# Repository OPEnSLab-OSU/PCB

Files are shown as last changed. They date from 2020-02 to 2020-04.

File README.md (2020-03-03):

# Project List
Opens Staff - Clone this repo and make a folder for your PCB. Once your PCB is added, place project links and update board file links here 

## [EAGLE Library Files](https://github.com/OPEnSLab-OSU/PCB/tree/master/OPEnS_Library)
Managed Libraries Folder *Coming Soon*

<!-- Copy an existing entry and add your project links directly below this comment -->
## [Sapflow](https://github.com/OPEnSLab-OSU/OPEnS-Lab-Home/wiki/Sap-Flow-Meter)

**New* V3 Board [Sapflow](https://github.com/OPEnSLab-OSU/PCB/tree/master/Sapflow)

## [Evaporometer](https://github.com/OPEnSLab-OSU/OPEnS-Lab-Home/wiki/Evaporometer)

INA125P Load Cell Amp [DevBoard](https://github.com/OPEnSLab-OSU/PCB/tree/master/Evaporometer_Lite/INA125P)

**New* Evaporometer V2 [V2.2 Board](https://github.com/OPEnSLab-OSU/PCB/tree/master/Evaporometer_Lite)

## [Hypnos](https://github.com/OPEnSLab-OSU/OPEnS-Hypnos)

**New* V3 Board [Hypnos 12V](https://github.com/OPEnSLab-OSU/PCB/tree/master/Hypnos)

## [PNNL Flux Tool](https://github.com/OPEnSLab-OSU/PNNLFluxV1)

Head [board](https://github.com/OPEnSLab-OSU/PCB/blob/master/PNNLFlux/Head-Board/head-board.brd),
[schematic](https://github.com/OPEnSLab-OSU/PCB/blob/master/PNNLFlux/Head-Board/head-board.sch)

Rod [board](https://github.com/OPEnSLab-OSU/PCB/blob/master/PNNLFlux/Rod-Board/rod-board.brd),
[schematic](https://github.com/OPEnSLab-OSU/PCB/blob/master/PNNLFlux/Rod-Board/rod-board.sch)

MS580302 [Pressure/EC sensor](https://github.com/OPEnSLab-OSU/PCB/tree/master/PNNLFlux/MS5803-02BA)

## [SmartRock](https://github.com/OPEnSLab-OSU/SmartRock)

MS580302 Pressure [MS5803](https://github.com/OPEnSLab-OSU/PCB/tree/master/SmartRock/MS5803), 
HydroPCB [HydroPCB](https://github.com/OPEnSLab-OSU/PCB/tree/master/SmartRock/HydroPCB)

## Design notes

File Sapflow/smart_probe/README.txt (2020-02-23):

This PCB attatches to the Sapflow project probe and makes it "smart".
It has a 3-channel ADC with analog lowpass filters in front of the inputs. 
It also has a differential I2C driver chip which can send I2C data from
the ADC over CAT V cables a couple meters long.

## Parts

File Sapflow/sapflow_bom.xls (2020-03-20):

PCB | Qty | Value | Device | Package | Parts | Description | Price | PN | Link
Smart Probe | 40 |  | Red LED | CHIP-LED0805 | LED1 | Red LED | 0.145 | 1080-EAST2012RA1CT-ND | https://www.digikey.com/product-detail/en/everlight-electronics-co-ltd/EAST2012RA1/1080-EAST2012RA1CT-ND/11201058
Smart Probe | 15 |  | Green LED | CHIP-LED0805 | LED2 | Green LED | 0.18 | 732-4983-1-ND | https://www.digikey.com/product-detail/en/w%C3%BCrth-elektronik/150080GS75000/732-4983-1-ND/4489913
Smart Probe | 100 | 0.1u | C-USC0805 | C0805 | C4, C6, C7, C8 | CAPACITOR, American symbol | 0.0286 | 1276-6476-1-ND | https://www.digikey.com/product-detail/en/samsung-electro-mechanics/CL21B154KBFNNNG/1276-6476-1-ND/5958104
Smart Probe | 100 | 1.5k | R-US_R0805 | R0805 | R17 | RESISTOR, American symbol | 0.0091 | RMCF0805FT1R62CT-ND | https://www.digikey.com/product-detail/en/stackpole-electronics-inc/RMCF0805FT1R62/RMCF0805FT1R62CT-ND/2418313
Smart Probe | 100 | 100 | R-US_R0805 | R0805 | R7 | RESISTOR, American symbol | 0.0104 | RMCF0805FT100RCT-ND | https://www.digikey.com/product-detail/en/stackpole-electronics-inc/RMCF0805FT100R/RMCF0805FT100RCT-ND/1942332
Smart Probe | 100 | 1u | C-USC0805 | C0805 | C1, C2, C3 | CAPACITOR, American symbol | 0.0281 | 1276-6471-1-ND | https://www.digikey.com/product-detail/en/samsung-electro-mechanics/CL21B105KOFNNNG/1276-6471-1-ND/5958099
Smart Probe | 100 | 40k | R-US_R0805 | R0805 | R1, R2, R3, R4, R14, R15 | RESISTOR, American symbol | 0.0104 | RMCF0805FT39K0CT-ND | https://www.digikey.com/product-detail/en/stackpole-electronics-inc/RMCF0805FT39K0/RMCF0805FT39K0CT-ND/2418387
Smart Probe | 100 | 47uF | C-USC0805 | C0805 | C5 | CAPACITOR, American symbol | 0.067 | 1276-1100-1-ND | https://www.digikey.com/product-detail/en/samsung-electro-mechanics/CL21A226MQQNNNE/1276-1100-1-ND/3889186
Smart Probe | 100 | 5k | R-US_R0805 | R0805 | R10, R11, R16 | RESISTOR, American symbol | 0.0104 | RMCF0805FT5K10CT-ND | https://www.digikey.com/product-detail/en/stackpole-electronics-inc/RMCF0805FT5K10/RMCF0805FT5K10CT-ND/1942416
Smart Probe | 100 | 910 | R-US_R0805 | R0805 | R5, R6, R8, R9 | RESISTOR, American symbol | 0.0104 | RMCF0805FT909RCT-ND | https://www.digikey.com/product-detail/en/stackpole-electronics-inc/RMCF0805FT909R/RMCF0805FT909RCT-ND/1942369
Smart Probe | 12 | MCP3424-E_SL | MCP3424-E_SL | SOIC127P600X175-14N | IC1 | ADC 18-Bit 4-ch 2.048V I2C SOIC14 | 3.91 | MCP3424-E/SL-ND | https://www.digikey.com/product-detail/en/microchip-technology/MCP3424-E-SL/MCP3424-E-SL-ND/1680890
Flex Probe | 100 | 100 | R-US_R0603 | R0603 | Heater resistor | RESISTOR, American symbol | 0.0065 | RMCF0603FT100RCT-ND | https://www.digikey.com/product-detail/en/stackpole-electronics-inc/RMCF0603FT100R/RMCF0603FT100RCT-ND/1942965
Flex Probe | 75 | PT100 | R-US_R0603 | R0603 | RTD | 100-ohm RTD | 1.2188 | PTS0603100CT-ND | https://www.digikey.com/products/en?keywords=PTS0603100CT-ND
Main PCB | 12 |  | NMOSSOT223 | SOT223 | T2 | MOS FET | 0.613 | FDT439NCT-ND | https://www.digikey.com/products/en?keywords=FDT439NCT-ND
Main PCB | 12 | 33uF | CPOL-USD/7343-31R | D/7343-31R | C8 | POLARIZED CAPACITOR, American symbol | 0.72 | 478-3047-1-ND | https://www.digikey.com/products/en?keywords=478-3047-1-ND
Main PCB | 12 | 47uF | CPOL-USD/7343-31R | D/7343-31R | C7 | POLARIZED CAPACITOR, American symbol | 0.628 | 478-3936-1-ND | https://www.digikey.com/products/en?keywords=478-3936-1-ND
Main PCB | 100 | 100pF | C-USC0805 | C0805 | C2 | CAPACITOR, American symbol | 0.0087 | 399-15000-1-ND | https://www.digikey.com/product-detail/en/kemet/C0805C101JAGAC7800/399-15000-1-ND/7382549
Main PCB | 12 | CR1220 | BATTERYCR1220_SMT | CR1220 | B1 | CR1220 SMT - Digikey: 3001K-ND | 0.44 | 36-3001-ND | https://www.digikey.com/products/en?keywords=3001K-ND
Main PCB | 12 | DS3231ST&R | DS3231ST&R | 21-0042B_16 | RTC | DS3231 RTC IC only | 7.576 | DS3231SN#T&RCT-ND | https://www.digikey.com/products/en?keywords=DS3231SN%23T%26RCT-ND
Main PCB | 12 | MAXIM_MAX5033BASA+MAXIM_MAX5033BASA+_0_1 | MAXIM_MAX5033BASA+MAXIM_MAX5033BASA+_0_1 | MAXIM_MAX5033BASA+_1 | U1 | MAX-MAX5033-IL8 | 2.71 | MAX5033BASA+-ND | https://www.digikey.com/products/en?keywords=MAX5033BASA%2B-ND
Main PCB | 12 | MICROSD | MICROSD | MICROSD | MICROSD | Micro-SD / Transflash card holder with SPI pinout | 1.95 | Adafruit 1660 | https://www.mouser.com/ProductDetail/Adafruit/1660?qs=sGAEpiMZZMsMyYRRhGMFNvyxRu5Civa4Xe9EwZhtNjo%3D
Main PCB | 50 | NMOS | NMOS | SOT23-S | Q1, Q4, Q5 | N-mos with low gate threshold | 0.1364 | BSS138-FDICT-ND | https://www.digikey.com/product-detail/en/diodes-incorporated/BSS138-7-F/BSS138-FDICT-ND/717843
Main PCB | 25 | PUSH_BUTTON | PUSH_BUTTON | PUSHBUTTON_SMD | U$1, U$2 | SMD low profile push-button | 0.321 | 611-KMR731NGLFS | https://www.mouser.com/ProductDetail/CK/KMR731NGLFS
Main PCB | 12 | SRR1208-102KL | SRR1208-102KL | IND_BOURNS_SRR1208 | L1 | Inductor | 1.047 | SRR1208-102KLCT-ND | https://www.digikey.com/product-detail/en/bourns-inc/SRR1208-102KL/SRR1208-102KLCT-ND/3437800
Main PCB | 25 | SSM3J3228R | SSM3J3228R | SOT-23-3 | PMOS1, PMOS2 | P-Channel MOSFET, SOT-23-3 SMD Package | 0.2452 | NTR4101PT1GOSCT-ND | https://www.digikey.com/product-detail/en/on-semiconductor/NTR4101PT1G/NTR4101PT1GOSCT-ND/687132
Main PCB | 25 | VS-50SQ100 | VS-50SQ100 | DIOAD1405W86L465D235 | D1, D2 | VS-50SQ100, Schottky Diode, 5A max, 100V, 2-Pin, DO-204AR | 0.242 | 1655-1519-1-ND | https://www.digikey.com/product-detail/en/smc-diode-solutions/SB240TA/1655-1519-1-ND/6022964
Other | 1 |  | Solder Paste | Syringe |  | Low-temp lead-free solder paste | 14.63 | 473-1269-ND | https://www.digikey.com/product-detail/en/mg-chemicals/4902P-15G/473-1269-ND/7496976

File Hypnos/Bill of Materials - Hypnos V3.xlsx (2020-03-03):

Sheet: Digikey
Source | Description | Units | Part number | Price/unit | Total | Purpose: X for Y
Digikey (https://www.digikey.com/products/en?keywords=DMP3099L-7DICT-ND) | P channel Mosfet | 2 | DMP3099L-7DICT-ND | 0.33 | 0.66 | Hypnos V3 | SOT23
Digikey (https://www.digikey.com/product-detail/en/diodes-incorporated/DMP3056LDM-7/DMP3056LDMDICT-ND/1964772) | P channel Mosfet - Large | 1 | DMP3056LDMDICT-ND | 0.41 | 0.41 | Hypnos V3 | 0805
Digikey (https://www.digikey.com/product-detail/en/diodes-incorporated/DMN65D8L-7/DMN65D8L-7DICT-ND/3677916) | N channel Mosfet | 2 | DMN65D8L-7DICT-ND | 0.17 | 0.34 | Hypnos V3 | SOT26
 |  |  |  |  |  |  | SOT23
Digikey (https://www.digikey.com/product-detail/en/yageo/RC0805FR-07100KL/311-100KCRCT-ND/730491) | 100k resistor 1% | 2 | 311-100KCRCT-ND | 0.1 | 0.2 | Hypnos V3
Digikey (https://www.digikey.com/product-detail/en/panasonic-electronic-components/ERJ-8GEYJ303V/P30KECT-ND/203313) | 30k resistor 5% | 2 | P30KECT-ND | 0.1 | 0.2 | Hypnos V3 | 1206
Adafruit (https://www.adafruit.com/product/1660) | microSD card socket | 1 | 1660 | 1.95 | 1.95 | Hypnos V3
Digikey (https://www.digikey.com/products/en?keywords=DS3231SN%23T%26RCT-ND) | DS3231 - works at -40C | 1 | DS3231SN#T&RCT-ND | 8.77 | 8.77 | Hypnos V3
Digikey (https://www.digikey.com/product-detail/en/c-k/KMR731NG-LFS/CKN10687CT-ND/6035359) | Push button | 2 | KMR731NG LFS | 0.34 | 0.68 | Hypnos V3 | SMD
Digikey (https://www.digikey.com/product-detail/en/keystone-electronics/3000TR/36-3000CT-ND/1532229) | Battery Holder 12mm | 1 | 36-3000CT-ND | 0.91 | 0.91 | Hypnos V3
Digikey (https://www.digikey.com/product-detail/en/te-connectivity-passive-product/CRGCQ1206J10K/A130183CT-ND/8578015) | 10k resistor 1% | 2 | A130183CT-ND | 0.10 | 0.10 | Hypnos V3 | 1206
Digikey (https://www.digikey.com/product-detail/en/yageo/CC1206KKX7R0BB104/311-1488-1-ND/2833794) | 0.1uF Capacitor | 2 | 311-1488-1-ND | 0.19 | 0.38 | Hypnos V3 | 1206
Digikey (https://www.digikey.com/product-detail/en/kingbright/APT2012LSECK-J3-PRV/754-1935-1-ND/5177465) | KingBright LED low current | 2 | 754-1935-1-ND | 0.51 | 1.02 | Hypnos V3 | 0805
Digikey (https://www.digikey.com/product-detail/en/stackpole-electronics-inc/RMCF1206FT3K00/RMCF1206FT3K00CT-ND/2418728) | 3K ohm resistor 1% | 1 | RMCF1206FT3K00CT-ND | 0.1 | 0.1 | Hypnos V3 | 1206
Digikey (https://www.digikey.com/product-detail/en/yageo/RC1206FR-076K2L/311-6.20KFRCT-ND/731963) | 6.2k ohm resistor 1% | 1 | 311-6.20KFRCT-ND | 0.1 | 0.1 | Hypnos V3 | 1206
Digikey (https://www.digikey.com/product-detail/en/kemet/C0805C101J5GACTU/399-1122-1-ND/411397) | 100pF Capacitor | 2 | 399-1122-1-ND | 0.1 | 0.2 | Hypnos V3 | 0805
Digikey (https://www.digikey.com/product-detail/en/micro-commercial-co/SM5817PL-TP/SM5817PL-TPMSCT-ND/1793410) | Schottky Diodes | 1 | SM5817PL-TPMSCT-ND | 0.44 | 0.44 | Hypnos V3
 |  |  |  | Total | 16.46

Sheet: Arrow
Source | Description | Units | Part number | Price/unit | Total | Purpose: X for Y
Arrow (https://www.arrow.com/en/products/dmn65d8l-7/diodes-incorporated) | N channel Mosfet | 1 | DMN65D8L-7 | 0.15 | 0.15 | Hypnos V2 |  | SOT23
Arrow (https://www.arrow.com/en/products/dmp3099l-7/diodes-incorporated) | P channel Mosfet | 2 | DMP3099L-7 | 0.31 | 0.62 | Hypnos V2 |  | SOT23
Digikey (https://www.digikey.com/product-detail/en/diodes-incorporated/DMP3056LDM-7/DMP3056LDMDICT-ND/1964772) | P channel Mosfet - Large | 1 | DMP3056LDMDICT-ND | 0.41 | 0.41 | Hypnos V3 |  |  | Not on Arrow
Arrow (https://www.arrow.com/en/products/rc1206fr-07100kl/yageo) | 100k resistor 1% | 2 | RC1206FR-07100KL | 0.1 | 0.2 | Hypnos V2 |  | 1206
Arrow (https://www.arrow.com/en/products/erj-8geyj303v/panasonic) | 30k resistor 5% | 2 | ERJ-8GEYJ303V | 0.1 | 0.2 | Hypnos V2 |  | 1206
Arrow (https://www.arrow.com/en/products/1660/adafruit-industries) | microSD card socket | 1 | 1660 | 2.32 | 2.32 | Hypnos V2 |  |  | Not on Arrow
Digikey (https://www.digikey.com/products/en?keywords=DS3231SN%23T%26RCT-ND) | DS3231 - works at -40C | 1 | DS3231SN#T&RCT-ND | 8.77 | 8.77 | Hypnos V2
Arrow (https://www.arrow.com/en/products/kmr731nglfs/ck) | Push button | 2 | KMR731NGLFS | 0.33 | 0.66 | Hypnos V2 |  | SMD | Min 100 order
Arrow (https://www.arrow.com/en/products/3000tr/keystone-electronics) | Battery Holder 12mm | 1 | 3000TR | 0.91 | 0.91 | Hypnos V2
Arrow (https://www.arrow.com/en/products/crgcq1206j10k/te-connectivity) | 10k resistor 1% | 2 | CRGCQ1206J10K | 0.09 | 0.18 | Hypnos V2 |  | 1206
Arrow (https://www.arrow.com/en/products/cc1206kkx7r0bb104/yageo) | 0.1uF Capacitor | 2 | CC1206KKX7R0BB104 | 0.18 | 0.36 | Hypnos V2 |  | 1206
Arrow (https://www.arrow.com/en/products/apt2012lseckj3-prv/kingbright) | KingBright LED low current | 2 | APT2012LSECK/J3-PRV | 0.43 | 0.86 | Hypnos V2 |  | 0805
Arrow (https://www.arrow.com/en/products/rmcf1206ft3k00/stackpole-electronics) | 3K ohm resistor 1% | 1 | RMCF1206FT3K00 | 0.1 | 0.1 | Hypnos V2 |  | 1206
Arrow (https://www.arrow.com/en/products/rc1206fr-076k2l/yageo) | 6.2k ohm resistor 1% | 1 | RC1206FR-076K2L | 0.1 | 0.1 | Hypnos V2 |  | 1206
Arrow (https://www.arrow.com/en/products/c0805c101j5gactu/kemet-corporation) | 100pF Capacitor | 2 | C0805C101J5GACTU | 0.1 | 0.2 | Hypnos V2 |  | 0805
Digikey (https://www.digikey.com/product-detail/en/micro-commercial-co/SM5817PL-TP/SM5817PL-TPMSCT-ND/1793410) | Schottky Diodes | 1 | SM5817PL-TPMSCT-ND | 0.44 | 0.44 | Hypnos V2 | Limit current leak from SD
 |  |  |  | Total | 16.48

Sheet: Mouser
Source | Description | Units | Part number | Price/unit | Total | Purpose: X for Y
Mouser (https://www.mouser.com/ProductDetail/Diodes-Incorporated/DMN65D8L-7) | N channel Mosfet | 2 | 621-DMN65D8L-7 | 0.16 | 0.32 | Hypnos V3 |  | SOT23
Mouser (https://www.mouser.com/ProductDetail/Diodes-Incorporated/DMP3099L-7) | P channel Mosfet | 2 | 621-DMP3099L-7 | 0.33 | 0.66 | Hypnos V3 |  | SOT23
Mouser (https://www.mouser.com/ProductDetail/Diodes-Incorporated/DMP3056LDM-7) | P channel Mosfet - Large | 1 | 621-DMP3056LDM-7 | 0.39 | 0.39 | Hypnos V3 |  | SOT26-6
Mouser (https://www.mouser.com/ProductDetail/Yageo/RC1206FR-07100KL) | 100k resistor 1% | 2 | 603-RC1206FR-07100KL | 0.1 | 0.2 | Hypnos V3 |  | 1206
Mouser (https://www.mouser.com/ProductDetail/Panasonic/ERJ-8GEYJ303V) | 30k resistor 5% | 2 | 667-ERJ-8GEYJ303V | 0.1 | 0.2 | Hypnos V3 |  | 1206
Mouser (https://www.mouser.com/ProductDetail/Adafruit/1660?qs=sGAEpiMZZMsMyYRRhGMFNvyxRu5Civa4Xe9EwZhtNjo%3D) | microSD card socket | 1 | 1660 | 1.95 | 1.95 | Hypnos V3
Mouser (https://www.mouser.com/ProductDetail/Maxim-Integrated/DS3231SNTR) | DS3231 - works at -40C | 1 | 700-DS3231SN#T&R- | 9.04 | 9.04 | Hypnos V3
Mouser (https://www.mouser.com/ProductDetail/CK/KMR731NGLFS) | Push button | 2 | 611-KMR731NGLFS | 0.34 | 0.68 | Hypnos V3 |  | SMD
Mouser (https://www.mouser.com/ProductDetail/Keystone-Electronics/3000TR?qs=sGAEpiMZZMsQtlBhqKq43UqKfTunsm6t) | Battery Holder 12mm | 1 | 534-3000TR | 0.91 | 0.91 | Hypnos V3
Mouser (https://www.mouser.com/ProductDetail/TE-Connectivity-Holsworthy/CRGCQ1206J10K) | 10k resistor 1% | 2 | 279-CRGCQ1206J10K | 0.15 | 0.3 | Hypnos V3 |  | 1206
Mouser (https://www.mouser.com/ProductDetail/Yageo/CC1206KKX7R0BB104) | 0.1uF Capacitor | 2 | 603-CC206KKX7R0BB104 | 0.26 | 0.52 | Hypnos V3 |  | 1206
Mouser (https://www.mouser.com/ProductDetail/Kingbright/APT2012LSECK-J3-PRV) | KingBright LED low current | 2 | 604-APT2012LSECKJ3RV | 0.5 | 1 | Hypnos V3 |  | 0805
Mouser (https://www.mouser.com/ProductDetail/Bourns/CR1206-FX-3001ELF?qs=sGAEpiMZZMu61qfTUdNhG6LqqFhkr6pUCgtUgzxqEks%3D) | 3K ohm resistor 1% | 1 | 652-CR1206FX-3001ELF | 0.1 | 0.1 | Hypnos V3 |  | 1206
Mouser (https://www.mouser.com/ProductDetail/Yageo/RC1206FR-076K2L?qs=sGAEpiMZZMu61qfTUdNhG6gKAQVNBKOoT1OSvDTEm5w%3D) | 6.2k ohm resistor 1% | 1 | 603-RC1206FR-076K2L | 0.23 | 0.23 | Hypnos V3 |  | 1206
Mouser (https://www.mouser.com/ProductDetail/KEMET/C0805C101J5GACTU) | 100pF Capacitor | 2 | 80-C0805C101J5G | 0.1 | 0.2 | Hypnos V3 |  | 0805
Mouser (https://www.mouser.com/ProductDetail/Micro-Commercial-Components-MCC/SM5817PL-TP) | Schottky Diodes | 1 | 833-SM5817PL-TP | 0.44 | 0.44 | Hypnos V3 | Limit current leak from SD
 |  |  |  | Total | 17.14 |  | Mouser is more expensive

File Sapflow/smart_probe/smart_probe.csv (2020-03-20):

Qty | Value | Device | Package | Parts | Description | ALLIED_NUMBER | ALLIED_PRICE-STOCK | DESCRIPTION | HEIGHT | MANUFACTURER_NAME | MANUFACTURER_PART_NUMBER | MF | MOUSER_PART_NUMBER | MOUSER_PRICE-STOCK | MPN | OC_FARNELL | OC_NEWARK | POPULARITY | RS_PART_NUMBER | RS_PRICE-STOCK | SPICEPREFIX
1 |  | I2C_STANDARD_NO_SILK | 1X04_NO_SILK | SPARKFUN | SparkFun I2C Standard Pinout Header
2 |  | LEDCHIP-LED0805 | CHIP-LED0805 | LED1, LED2 | LED |  |  |  |  |  |  |  |  |  |  |  |  | 68
1 |  | MA03-2 | MA03-2 | INPUT | PIN HEADER |  |  |  |  |  |  |  |  |  |  | unknown | unknown | 15
1 |  | MA04-2 | MA04-2 | PROBE | PIN HEADER |  |  |  |  |  |  |  |  |  |  | unknown | unknown | 11
4 |  | SJ | SJ | SJ1, SJ2, SJ3, SJ4 | SMD solder JUMPER |  |  |  |  |  |  |  |  |  |  |  |  | 33
4 | 0.1u | C-USC0805 | C0805 | C4, C6, C7, C8 | CAPACITOR, American symbol |  |  |  |  |  |  |  |  |  |  |  |  | 63 |  |  | C
1 | 1.5k | R-US_R0805 | R0805 | R17 | RESISTOR, American symbol |  |  |  |  |  |  |  |  |  |  |  |  | 85 |  |  | R
1 | 100 | R-US_R0805 | R0805 | R7 | RESISTOR, American symbol |  |  |  |  |  |  |  |  |  |  |  |  | 85 |  |  | R
3 | 1u | C-USC0805 | C0805 | C1, C2, C3 | CAPACITOR, American symbol |  |  |  |  |  |  |  |  |  |  |  |  | 63 |  |  | C
6 | 40k | R-US_R0805 | R0805 | R1, R2, R3, R4, R14, R15 | RESISTOR, American symbol |  |  |  |  |  |  |  |  |  |  |  |  | 85 |  |  | R
1 | 47uF | C-USC0805 | C0805 | C5 | CAPACITOR, American symbol |  |  |  |  |  |  |  |  |  |  |  |  | 63 |  |  | C
3 | 5k | R-US_R0805 | R0805 | R10, R11, R16 | RESISTOR, American symbol |  |  |  |  |  |  |  |  |  |  |  |  | 85 |  |  | R
4 | 910 | R-US_R0805 | R0805 | R5, R6, R8, R9 | RESISTOR, American symbol |  |  |  |  |  |  |  |  |  |  |  |  | 85 |  |  | R
1 | MCP3424-E_SL | MCP3424-E_SL | SOIC127P600X175-14N | IC1 | ADC 18-Bit 4-ch 2.048V I2C SOIC14 | 70046797 | http://www.alliedelec.com/microchip-technology-inc-mcp3424-e-sl/70046797/ | ADC 18-Bit 4-ch 2.048V I2C SOIC14 | 1.75mm | Microchip | MCP3424-E/SL |  | 579-MCP3424-E/SL | https://www.mouser.com/Search/Refine.aspx?Keyword=579-MCP3424-E%2FSL |  |  |  |  | 6696086P | http://uk.rs-online.com/web/p/products/6696086P

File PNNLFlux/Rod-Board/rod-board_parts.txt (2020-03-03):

Partlist

Exported from rod-board.brd at 12/20/19 8:15 AM

EAGLE Version 9.5.1 Copyright (c) 1988-2019 Autodesk, Inc.

Assembly variant: 

Part     Value          Package          Library             Position (inch)       Orientation

A1       ADS1115        ADS1115          PNNL_Probe          (0.7 3.3)             R90
A2       TCA9548A       TCA9548A         PNNL_Probe          (0 4.45)              R0
A3       DS3502         DS3502           PNNL_Probe          (0.7 2.25)            R90
ACOUT    PTR1PAD1-13    P1-13            testpad             (0.6 1.2)             R0
AOUT     PTR1PAD1-13    P1-13            testpad             (0.6 2.1)             R0
C1       100nF          C1206            rcl                 (0.45 0.75)           R270
C2       100nF          C1206            rcl                 (0.6 1)               R90
C3       100nF          C1206            rcl                 (0.15 1.25)           R90
C4       1uF            C1206            rcl                 (0.3 1.65)            R270
C5       1uF            C1206            rcl                 (0.6 1.65)            R90
C6       1uF            C1206            rcl                 (0.6 1.9)             R90
C7       0.1uF          0603             SparkFun-Capacitors (0.25 5.6)            R270
C9       1.0uF          0603             SparkFun-Capacitors (0.45 5.6)            R270
C16      1uF            C1206            rcl                 (0.15 2.4)            R270
C17      1uF            C1206            rcl                 (0.3 2.4)             R270
C18      1uF            C1206            rcl                 (0.45 2.4)            R270
D1       1N4001         D-5              diode               (0.3 1)               R270
D2       1N4001         D-5              diode               (0.15 1)              R90
D3       1N4001         D-5              diode               (0.35 1.45)           R0
D4       1N4001         D-5              diode               (0.45 2.15)           R90
D5       1N4001         D-5              diode               (0.3 2.15)            R270
IC1      CD4051BE       CD4051BE         PNNL_Probe          (0.15 3.45)           MR90
IC2      TL074P         DIL14            linear              (0.35 3)              MR90
IC3      MCP23008       MCP23008         PNNL_Probe          (0.1 4.25)            MR90
J3       RJ45           RJ45-8           SparkFun-Connectors (0.35 6.1)            R180
JP1                     1X03             pinhead             (0.2 0.1)             R0
JP2                     1X03             pinhead             (0.5 0.1)             R0
JP3                     1X03             pinhead             (0.2 0.3)             R0
JP4                     1X03             pinhead             (0.5 0.3)             R0
JP5                     1X03             pinhead             (0.2 0.5)             R0
JP6                     1X02             pinhead             (0.55 0.5)            R0
PIN6     PTR1PAD1-13    P1-13            testpad             (0.6 3.2)             MR0
PIN7     PTR1PAD1-13    P1-13            testpad             (0.1 3.1)             MR0
PIN12    PTR1PAD1-13    P1-13            testpad             (0.6 1.45)            R0
R1       1K             R1206            rcl                 (0.6 0.75)            R90
R2       10K            R1206            rcl                 (0.3 0.75)            R270
R3       22K            R1206            rcl                 (0.15 0.75)           R90
R4       1K             R1206            rcl                 (0.45 1)              R90
R5       2K             R1206            rcl                 (0.3 1.25)            R90
R6       1K             R1206            rcl                 (0.45 1.25)           R270
R7       10K            R1206            rcl                 (0.15 1.65)           R270
R8       4.7K           R1206            rcl                 (0.45 1.65)           R270
R9       10K            R1206            rcl                 (0.3 1.9)             R90
R10      5K             R1206            rcl                 (0.15 1.9)            R270
R11      4.7K           R1206            rcl                 (0.45 1.9)            R90
R13      390            0603             SparkFun-Resistors  (0.55 5.6)            R90
R14      100            0603             SparkFun-Resistors  (0.55 5.45)           R90
R15      390            0603             SparkFun-Resistors  (0.55 5.3)            R90
R16      390            0603             SparkFun-Resistors  (0.15 5.6)            R90
R17      100            0603             SparkFun-Resistors  (0.15 5.45)           R90
R18      390            0603             SparkFun-Resistors  (0.15 5.3)            R90
R19      4.7k           0603             SparkFun-Resistors  (0.25 5.2)            R0
R20      4.7k           0603             SparkFun-Resistors  (0.45 5.2)            R180
U1       PCA9615        TSSOP10          SparkFun-IC-Comms   (0.35 5.4)            R0
U2       TPS60400DBVR   SOT95P280X145-5N TPS60400DBVR        (0.1 2.15)            R90
VCC1     PTR1PAD1-13    P1-13            testpad             (0.6 2.35)            MR270
VNEG1    PTR1PAD1-13    P1-13            testpad             (0.1 3)               MR0
WEIN     PTR1PAD1-13    P1-13            testpad             (0.15 1.45)           R0

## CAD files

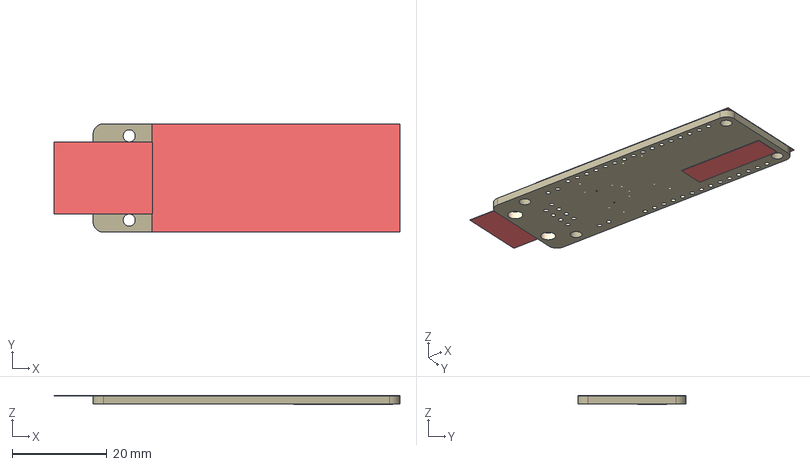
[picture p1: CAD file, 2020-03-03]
PNNLFlux/Head-Board/head-board_fixed.step
73.0 x 22.9 x 1.87 mm
Board
HYPNOS_CONNECTION
1.0uF x 2
RJ45
4.7k x 8
OPENS-LOGO
PCA9615

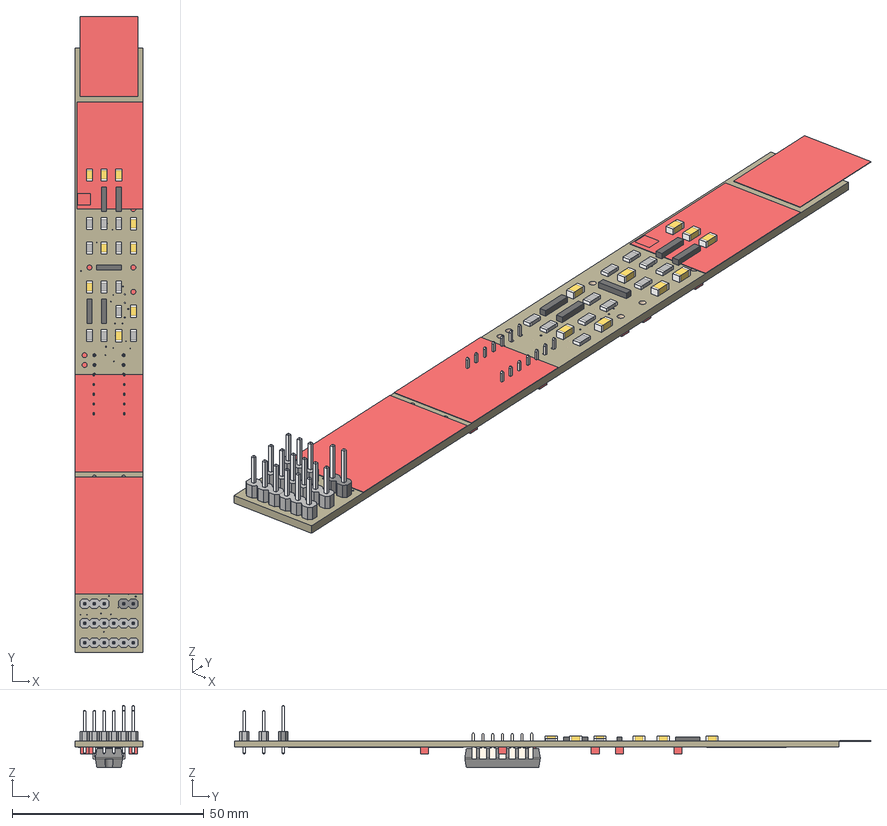
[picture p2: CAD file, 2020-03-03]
PNNLFlux/Rod-Board/rod-board.step
17.8 x 165.7 x 16.2 mm
Board
ADS1115
CD4051BE
TCA9548A
SENSOR4 x 5
POWER
4.7K x 11
1uF x 9
TL074P
PTR1PAD1-13 x 8
1N4001 x 5
TPS60400DBVR
PCA9615
4.7k_1 x 8
1.0uF x 2
RJ45
OPENS-LOGO
DS3502
MCP23008

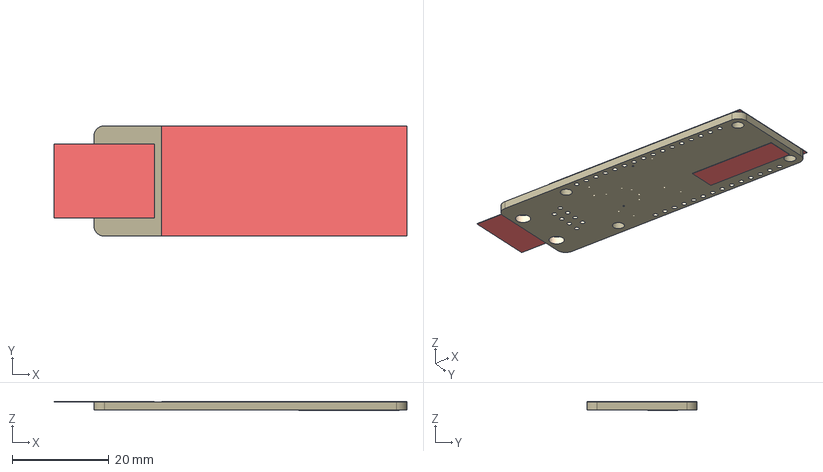
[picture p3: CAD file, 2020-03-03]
PNNLFlux/Head-Board/head-board.step
73.0 x 22.9 x 1.87 mm
Board
HYPNOS_CONNECTION
1.0uF x 2
RJ45
4.7k x 8
OPENS-LOGO
PCA9615

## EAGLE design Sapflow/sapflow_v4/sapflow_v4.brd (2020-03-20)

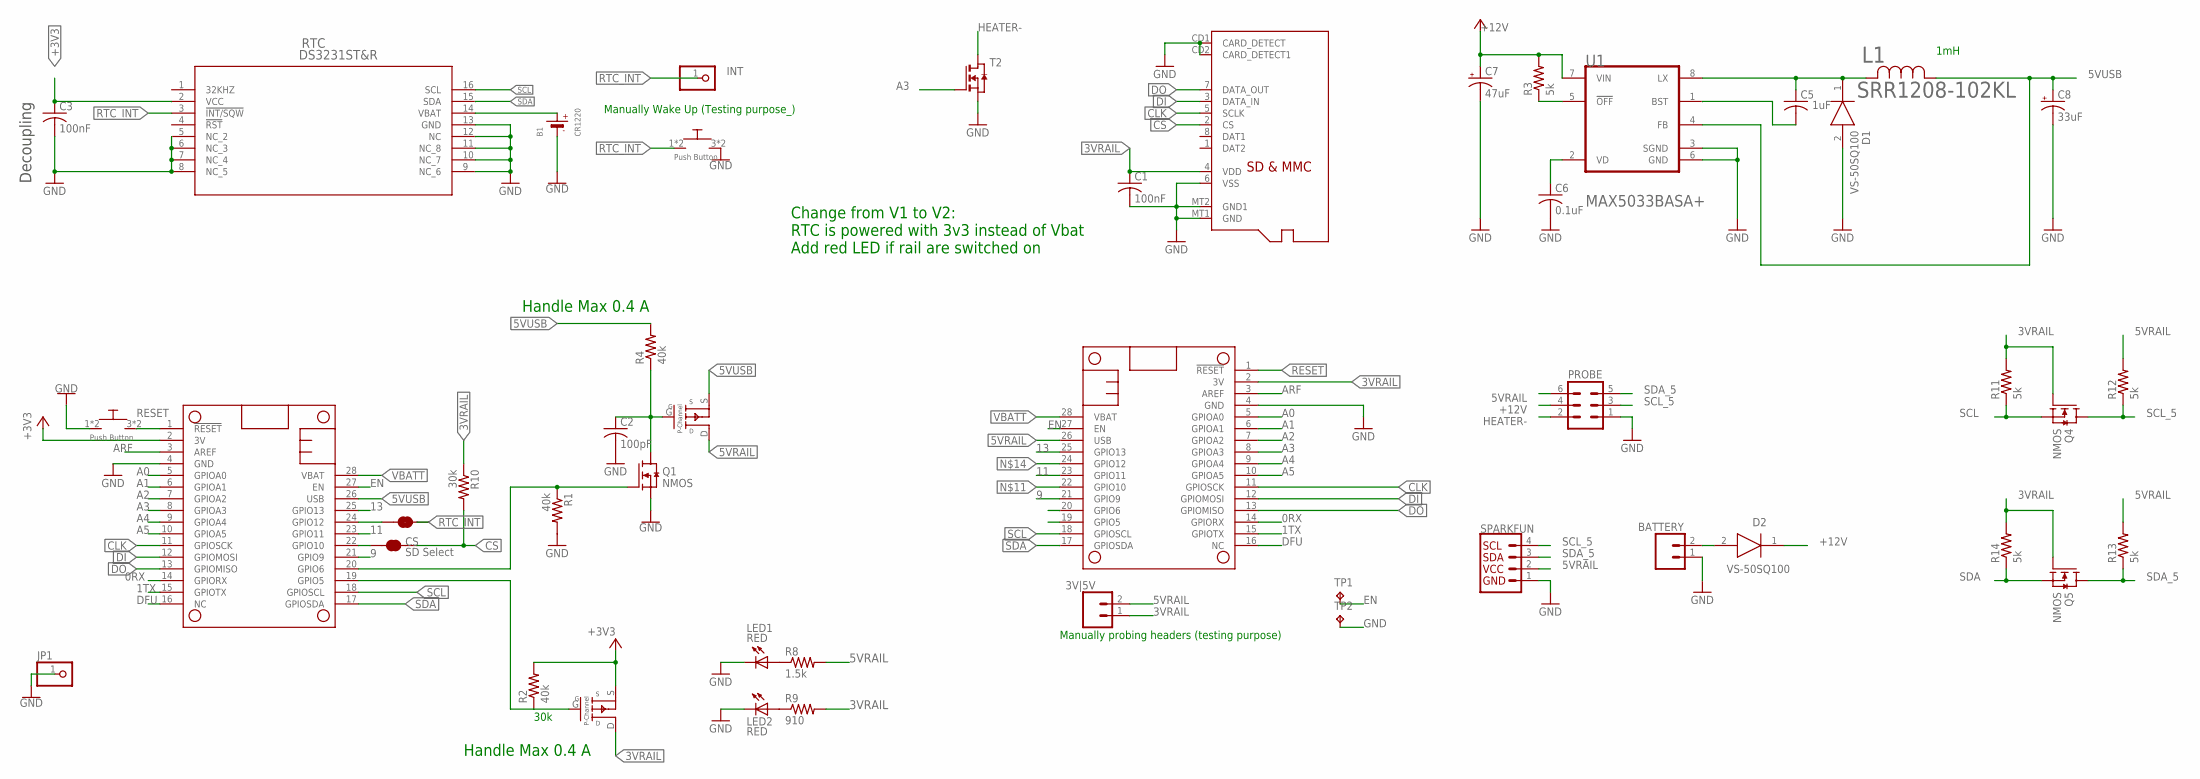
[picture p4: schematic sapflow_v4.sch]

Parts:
3V|5V: CONN_021X02_NO_SILK; 1X02_NO_SILK
B1: CR1220
BATTERY: HIGHV-OUT; 1X02_NO_SILK
C1, C3: 100nF; C0805
C2: 100pF; C0805
C5: 1uF; C0805
C6: 0.1uF; C0805
C7: 47uF; D/7343-31R
C8: 33uF; D/7343-31R
CS: SD Select; SMT-JUMPER_2_NC_TRACE_SILK
D1, D2: VS-50SQ100; DIOAD1405W86L465D235
INT: PINHD-1X1CB; 1X01-CLEANBIG
JP1: PINHD-1X1CB; 1X01-CLEANBIG
L1: SRR1208-102KL; IND_BOURNS_SRR1208
LED1, LED2: RED; CHIPLED_0805
MICROSD: MICROSD
MS1, MS2: FEATHERWING
PMOS1, PMOS2: SSM3J3228R; SOT-23-3
PROBE: MA03-2
Q1, Q4, Q5: NMOS; SOT23-S
R1, R2, R4: 40k; R0805
R3, R11, R12, R13, R14: 5k; R0805
R8: 1.5k; R0805
R9: 910; R0805
R10: 30k; R0805
RTC: DS3231ST&R; 21-0042B_16
RTC_INT: JUMPER-SMT_2_NC_TRACE_SILK; SMT-JUMPER_2_NC_TRACE_SILK
SPARKFUN: I2C_STANDARD_NO_SILK; 1X04_NO_SILK
T2: NMOSSOT223; SOT223
TP1, TP2: TPTP16R; TP16R
U1: MAXIM_MAX5033BASA+MAXIM_MAX5033BASA+_0_1; MAXIM_MAX5033BASA+_1
U$1, U$2: PUSH_BUTTON; PUSHBUTTON_SMD

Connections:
0RX: MS1.14 (GPIORX), MS2.14 (GPIORX)
1TX: MS1.15 (GPIOTX), MS2.15 (GPIOTX)
3VRAIL: 3V|5V.1, C1.1, MICROSD.4 (VDD), MS1.2 (3V), PMOS2.D, Q4.1 (G), Q5.1 (G), R9.2, R10.1, R11.2, R14.2
5VRAIL: 3V|5V.2, MS1.26 (USB), PMOS1.D, PROBE.6, R8.2, R12.2, R13.2, SPARKFUN.2 (VCC)
5VUSB: C8.+, L1.1, MS2.26 (USB), PMOS1.S, R4.2, U1.4 (FB)
9: MS1.21 (GPIO9), MS2.21 (GPIO9)
11: MS1.23 (GPIO11), MS2.23 (GPIO11)
13: MS1.25 (GPIO13), MS2.25 (GPIO13)
+3V3: C3.1, MS2.2 (3V), PMOS2.S, R2.2, RTC.2 (VCC)
+12V: C7.+, D2.1 (K), PROBE.4, R3.2, U1.7 (VIN)
A0: MS1.5 (GPIOA0), MS2.5 (GPIOA0)
A1: MS1.6 (GPIOA1), MS2.6 (GPIOA1)
A2: MS1.7 (GPIOA2), MS2.7 (GPIOA2)
A3: MS1.8 (GPIOA3), MS2.8 (GPIOA3), T2.1 (G)
A4: MS1.9 (GPIOA4), MS2.9 (GPIOA4)
A5: MS1.10 (GPIOA5), MS2.10 (GPIOA5)
ARF: MS1.3 (AREF), MS2.3 (AREF)
CLK: MICROSD.5 (SCLK), MS1.11 (GPIOSCK), MS2.11 (GPIOSCK)
CS: CS.2, MICROSD.2 (CS), R10.2
DFU: MS1.16 (NC), MS2.16 (NC)
DI: MICROSD.3 (DATA_IN), MS1.12 (GPIOMOSI), MS2.12 (GPIOMOSI)
DO: MICROSD.7 (DATA_OUT), MS1.13 (GPIOMISO), MS2.13 (GPIOMISO)
EN: MS1.27 (EN), MS2.27 (EN), TP1.TP
GND: B1.-, BATTERY.1, C1.2, C2.2, C3.2, C6.2, C7.-, C8.-, D1.2 (A), JP1.1, LED1.C, LED2.C, MICROSD.6 (VSS), MICROSD.CD1 (CARD_DETECT), MICROSD.CD2 (CARD_DETECT1), MICROSD.MT1 (GND), MICROSD.MT2 (GND1), MS1.4 (GND), MS2.4 (GND), PROBE.1, Q1.2 (S), R1.2, RTC.5 (NC_2), RTC.6 (NC_3), RTC.7 (NC_4), RTC.8 (NC_5), RTC.9 (NC_6), RTC.10 (NC_7), RTC.11 (NC_8), RTC.12 (NC), RTC.13 (GND), SPARKFUN.1 (GND), T2.3 (S), TP2.TP, U1.3 (SGND), U1.6 (GND), U$1.1, U$1.2, U$2.3, U$2.4
HEATER-: PROBE.2, T2.2 (D), T2.4 (D)
unnamed: MS2.20 (GPIO6), Q1.1 (G), R1.1
unnamed: B1.+$1 (+), RTC.14 (VBAT)
unnamed: MS2.19 (GPIO5), PMOS2.G, R2.1
unnamed: BATTERY.2, D2.2 (A)
unnamed: C6.1, U1.2 (VD)
unnamed: R3.1, U1.5 (!OFF!)
unnamed: C2.1, PMOS1.G, Q1.3 (D), R4.1
unnamed: CS.1, MS1.22 (GPIO10), MS2.22 (GPIO10)
unnamed: LED1.A, R8.1
unnamed: LED2.A, R9.1
unnamed: MS1.24 (GPIO12), MS2.24 (GPIO12), RTC_INT.1
unnamed: C5.2, U1.1 (BST)
unnamed: C5.1, D1.1 (K), L1.2, U1.8 (LX)
RESET: MS1.1 (!RESET), MS2.1 (!RESET), U$1.3, U$1.4
RTC_INT: INT.1, RTC.3 (!INT/SQW), RTC_INT.2, U$2.1, U$2.2
SCL: MS1.18 (GPIOSCL), MS2.18 (GPIOSCL), Q4.2 (S), R11.1, RTC.16 (SCL)
SCL_5: PROBE.3, Q4.3 (D), R12.1, SPARKFUN.4 (SCL)
SDA: MS1.17 (GPIOSDA), MS2.17 (GPIOSDA), Q5.2 (S), R14.1, RTC.15 (SDA)
SDA_5: PROBE.5, Q5.3 (D), R13.1, SPARKFUN.3 (SDA)
VBATT: MS1.28 (VBAT), MS2.28 (VBAT)

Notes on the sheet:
Decoupling
Manually Wake Up (Testing purpose_)
Manually probing headers (testing purpose)
30k
Change from V1 to V2: RTC is powered with 3v3 instead of Vbat Add red LED if rail are switched on
Handle Max 0.4 A
1mH

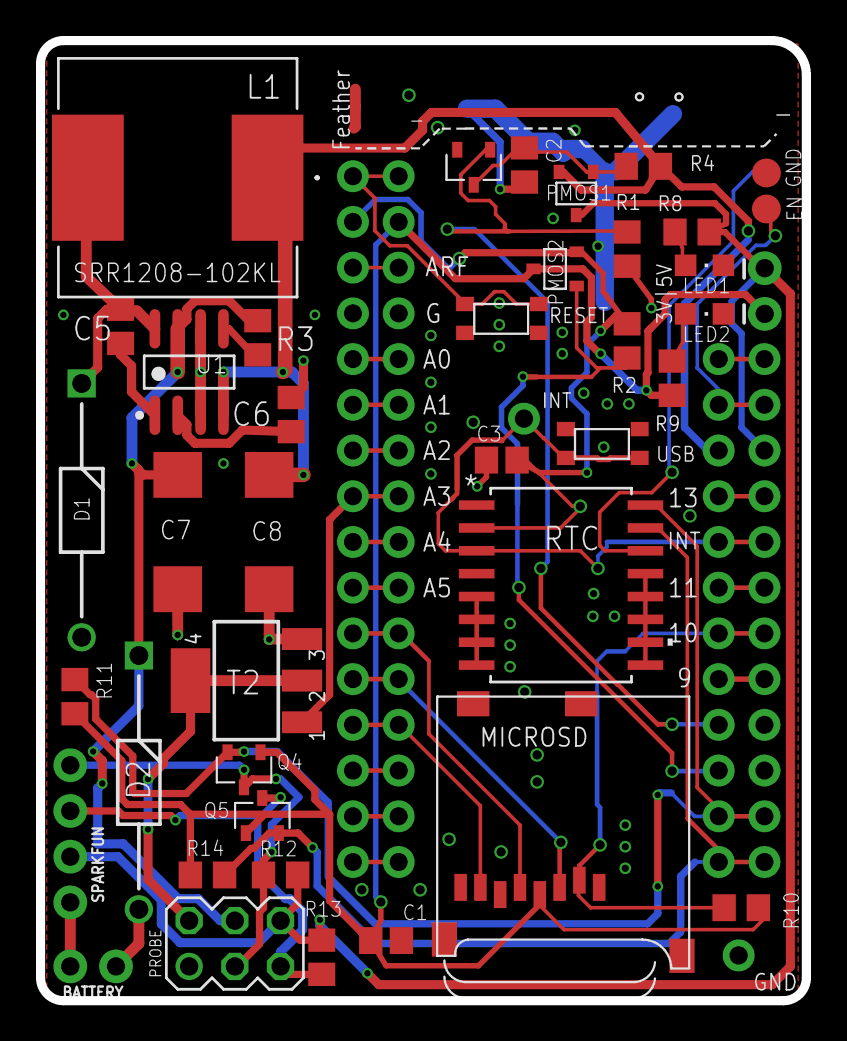
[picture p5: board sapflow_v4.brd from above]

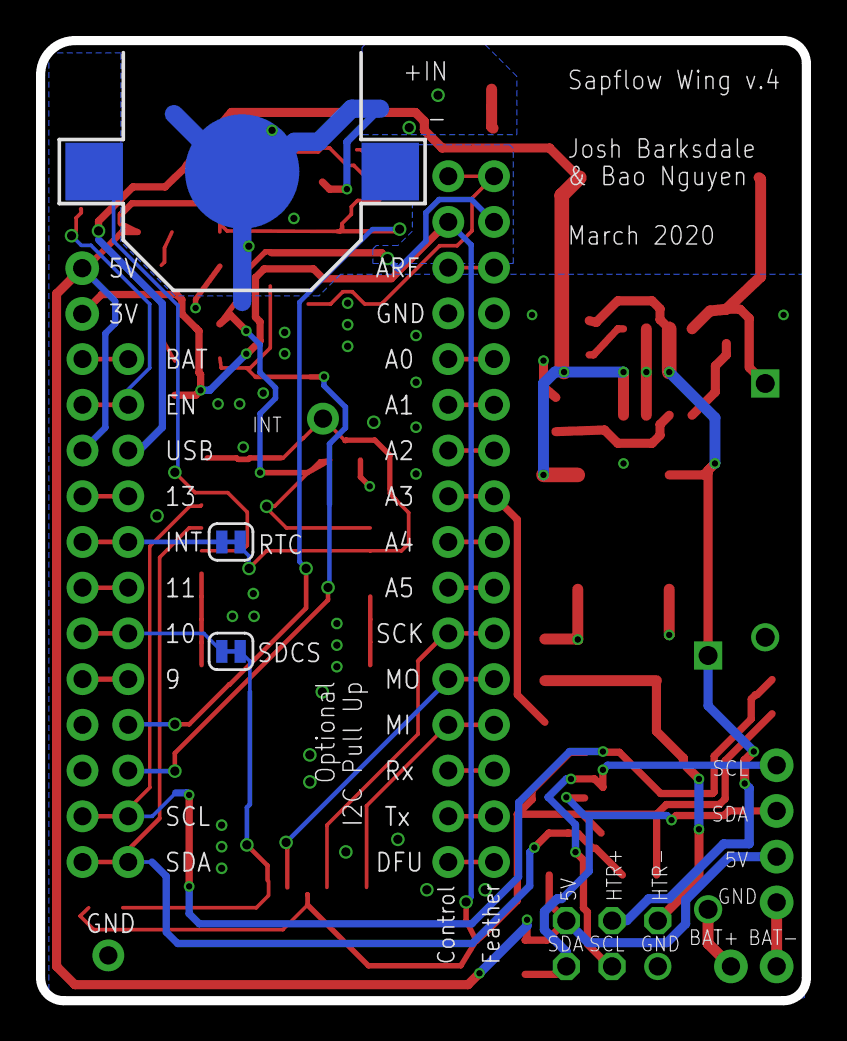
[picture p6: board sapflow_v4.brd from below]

Board: 2 copper layers, 42.5 x 53.3 mm, 47 parts (4 on the bottom side), 45 nets.

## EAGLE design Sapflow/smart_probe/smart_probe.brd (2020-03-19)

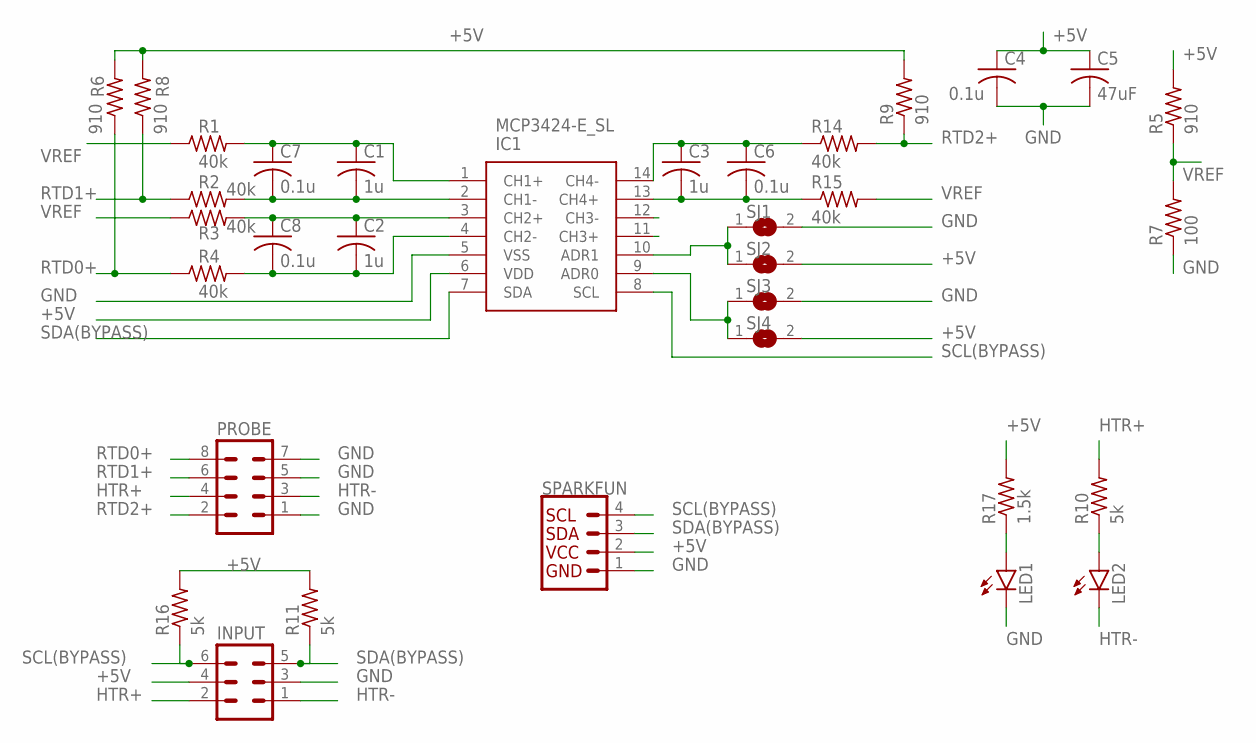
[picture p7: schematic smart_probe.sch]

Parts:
C1, C2, C3: 1u; C0805
C4, C6, C7, C8: 0.1u; C0805
C5: 47uF; C0805
IC1: MCP3424-E_SL; SOIC127P600X175-14N
INPUT: MA03-2
LED1, LED2: LEDCHIP-LED0805; CHIP-LED0805
PROBE: MA04-2
R1, R2, R3, R4, R14, R15: 40k; R0805
R5, R6, R8, R9: 910; R0805
R7: 100; R0805
R10, R11, R16: 5k; R0805
R17: 1.5k; R0805
SJ1, SJ2, SJ3, SJ4: SJ
SPARKFUN: I2C_STANDARD_NO_SILK; 1X04_NO_SILK

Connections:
+5V: C4.1, C5.1, IC1.6 (VDD), INPUT.4, R5.2, R6.2, R8.2, R9.2, R11.2, R16.2, R17.2, SJ2.2, SJ4.2, SPARKFUN.2 (VCC)
CH1+: C1.1, C7.1, IC1.1 (CH1+), R1.2
CH1-: C1.2, C7.2, IC1.2 (CH1-), R2.2
CH2+: C2.1, C8.1, IC1.3 (CH2+), R3.2
CH2-: C2.2, C8.2, IC1.4 (CH2-), R4.2
CH3+: IC1.11 (CH3+)
CH3-: IC1.12 (CH3-)
CH4+: C3.2, C6.2, IC1.13 (CH4+), R15.1
CH4-: C3.1, C6.1, IC1.14 (CH4-), R14.1
GND: C4.2, C5.2, IC1.5 (VSS), INPUT.3, LED1.C, PROBE.1, PROBE.5, PROBE.7, R7.1, SJ1.2, SJ3.2, SPARKFUN.1 (GND)
HTR+: INPUT.2, PROBE.4, R10.2
HTR-: INPUT.1, LED2.C, PROBE.3
unnamed: LED1.A, R17.1
unnamed: LED2.A, R10.1
unnamed: IC1.10 (ADR1), SJ1.1, SJ2.1
unnamed: IC1.9 (ADR0), SJ3.1, SJ4.1
RTD0+: PROBE.8, R4.1, R6.1
RTD1+: PROBE.6, R2.1, R8.1
RTD2+: PROBE.2, R9.1, R14.2
SCL(BYPASS): IC1.8 (SCL), INPUT.6, R16.1, SPARKFUN.4 (SCL)
SDA(BYPASS): IC1.7 (SDA), INPUT.5, R11.1, SPARKFUN.3 (SDA)
VREF: R1.1, R3.1, R5.1, R7.2, R15.2

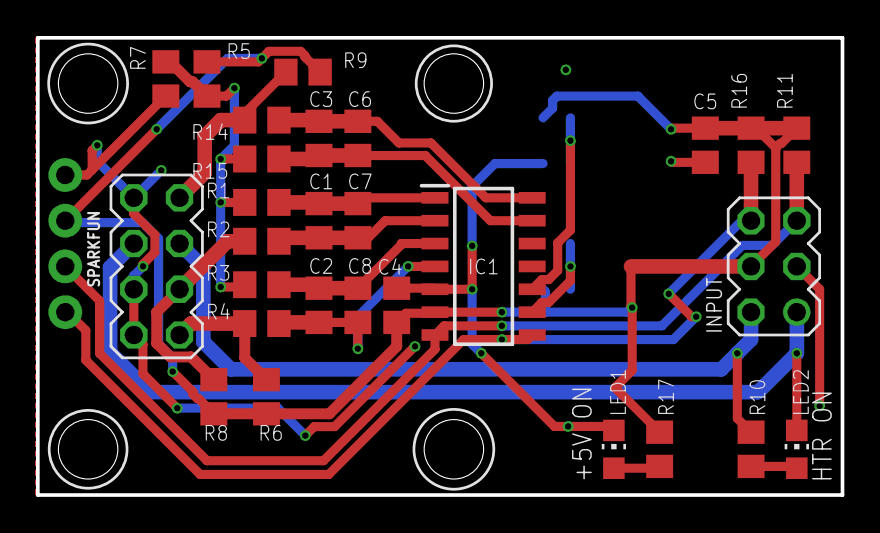
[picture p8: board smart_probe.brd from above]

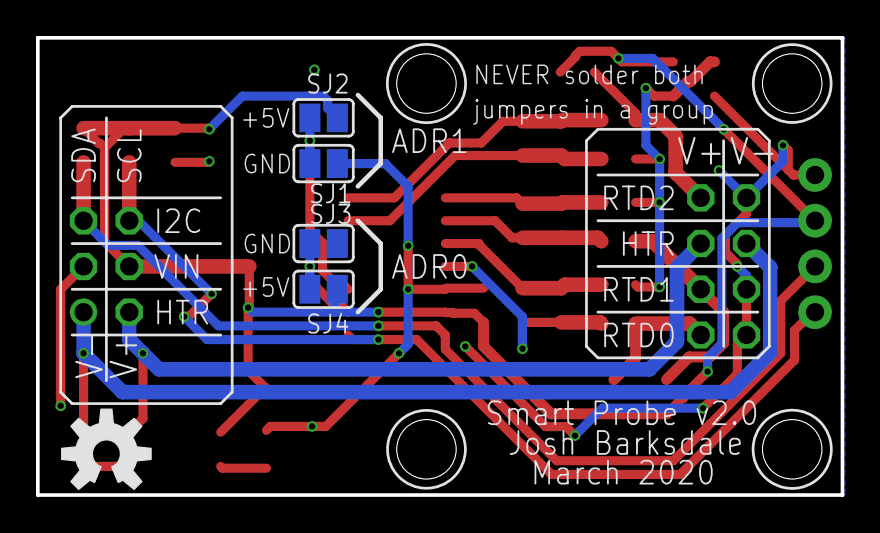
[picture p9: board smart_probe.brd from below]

Board: 2 copper layers, 44.7 x 25.4 mm, 38 parts (5 on the bottom side), 20 nets.

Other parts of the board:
H1, H2, H3, H4: STAND-OFF
LOGO1: OSHW-LOGOM; OSHW-LOGO-M

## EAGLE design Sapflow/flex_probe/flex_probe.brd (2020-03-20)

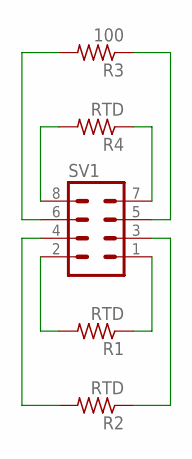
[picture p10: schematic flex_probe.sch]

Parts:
R1, R2, R4: RTD; R0603
R3: 100; R0603
SV1: MA04-2

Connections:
unnamed: R1.2, SV1.2
unnamed: R1.1, SV1.1
unnamed: R2.2, SV1.4
unnamed: R2.1, SV1.3
unnamed: R4.1, SV1.7
unnamed: R3.2, SV1.6
unnamed: R3.1, SV1.5
unnamed: R4.2, SV1.8

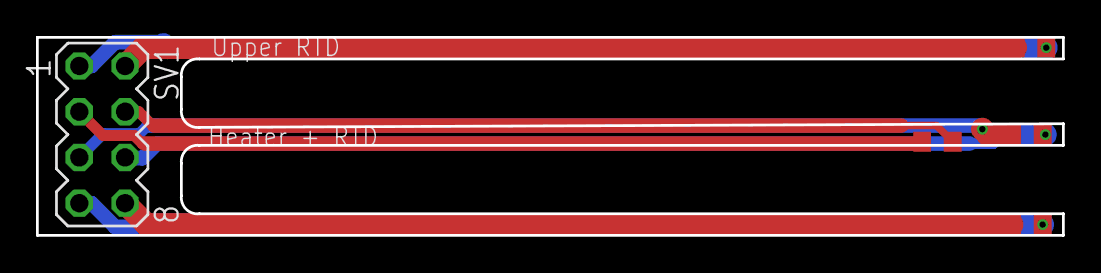
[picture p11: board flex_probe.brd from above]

Board: 2 copper layers, 57.0 x 11.0 mm, 5 parts (0 on the bottom side), 8 nets.

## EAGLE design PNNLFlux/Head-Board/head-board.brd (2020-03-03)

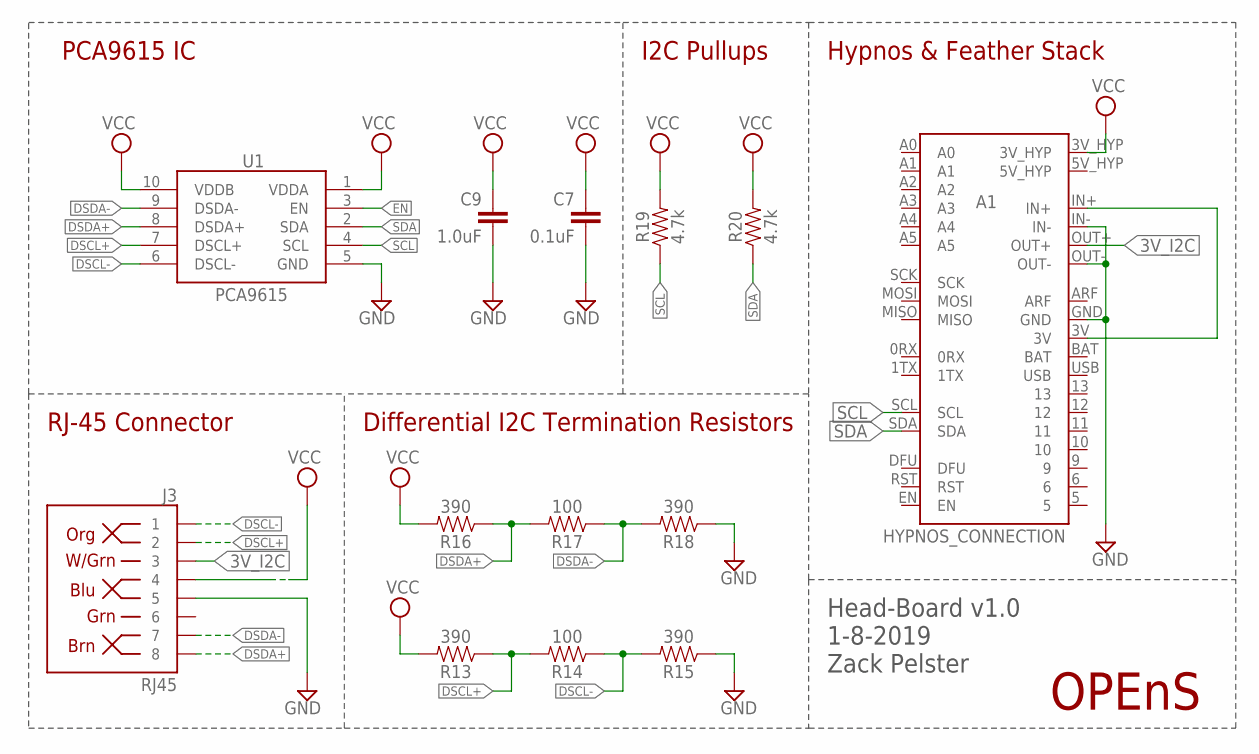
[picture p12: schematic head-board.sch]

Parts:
A1: HYPNOS_CONNECTION
C7: 0.1uF; 0603
C9: 1.0uF; 0603
J3: RJ45; RJ45-8
R13, R15, R16, R18: 390; 0603
R14, R17: 100; 0603
R19, R20: 4.7k; 0603
U1: PCA9615; TSSOP10
U$1: OPENS-LOGO

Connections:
3V_I2C: A1.OUT+, J3.3
BAT: A1.BAT
DSCL+: J3.2, R13.1, R14.2, U1.7 (DSCL+)
DSCL-: J3.1, R14.1, R15.2, U1.6 (DSCL-)
DSDA+: J3.8, R16.1, R17.2, U1.8 (DSDA+)
DSDA-: J3.7, R17.1, R18.2, U1.9 (DSDA-)
EN: U1.3 (EN)
GND: A1.GND, A1.IN-, A1.OUT-, C7.2, C9.2, J3.5, R15.1, R18.1, U1.5 (GND)
unnamed: A1.3V, A1.IN+
SCL: A1.SCL, R19.1, U1.4 (SCL)
SDA: A1.SDA, R20.1, U1.2 (SDA)
USB: A1.USB
VCC: A1.3V_HYP, C7.1, C9.1, J3.4, R13.2, R16.2, R19.2, R20.2, U1.1 (VDDA), U1.10 (VDDB)

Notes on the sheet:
PCA9615 IC
I2C Pullups
RJ-45 Connector
Differential I2C Termination Resistors
Head-Board v1.0 1-8-2019 Zack Pelster
Hypnos & Feather Stack

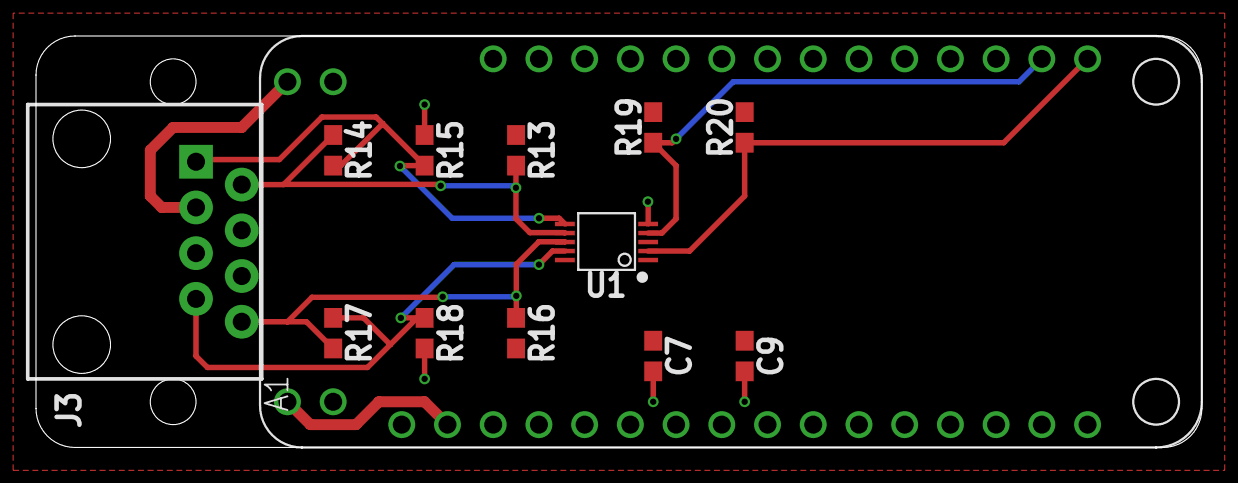
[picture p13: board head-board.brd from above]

Board: 2 copper layers, 64.8 x 22.9 mm, 14 parts (1 on the bottom side), 10 nets.

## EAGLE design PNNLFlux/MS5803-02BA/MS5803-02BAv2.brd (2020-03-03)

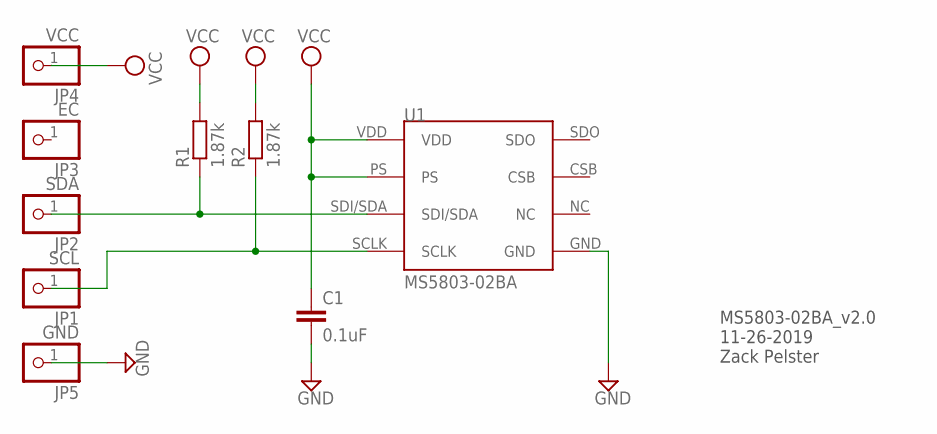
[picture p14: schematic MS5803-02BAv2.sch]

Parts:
C1: 0.1uF; C0805
JP1: SCL; 1X01
JP2: SDA; 1X01
JP3: EC; 1X01
JP4: VCC; 1X01
JP5: GND; 1X01
R1, R2: 1.87k; R0805
U1: MS5803-02BA

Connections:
GND: C1.2, JP5.1, U1.GND
unnamed: JP2.1, R1.1, U1.SDI/SDA
unnamed: JP1.1, R2.1, U1.SCLK
VCC: C1.1, JP4.1, R1.2, R2.2, U1.PS, U1.VDD

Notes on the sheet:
MS5803-02BA_v2.0 11-26-2019 Zack Pelster

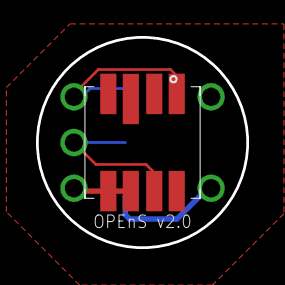
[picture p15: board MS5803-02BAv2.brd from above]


Board: 2 copper layers, 11.7 x 11.7 mm, 9 parts (3 on the bottom side), 4 nets.

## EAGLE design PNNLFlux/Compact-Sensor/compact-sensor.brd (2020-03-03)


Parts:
C1, C2, C3: 100nF; C0603
C4, C5, C6, C16, C17, C18: 1uF; C0603
C7, C8, C10, C11: 0.1uF; C0603
C9: 1.0uF; C0603
D1, D2, D3, D4, D5: 1N4001; SOD123
IC2: TL074D; SO14
J1, J3: RJ45; RJ45-8
JP1: EC; 1X01
JP2: GND; 1X01
R1, R4, R6: 1K; R0603
R2, R7, R9: 10K; R0603
R3: 22K; R0603
R5: 2K; R0603
R8, R11: 4.7K; R0603
R10: 5K; R0603
R12, R21: 10k; R0603
R13, R15, R16, R18: 390; R0603
R14, R17: 100; R0603
R19, R20: 4.7k; R0603
RHB: 280k; R0603
RHT: 1000k; R0603
RLB: 102k; R0603
RLT: 976k; R0603
U1: PCA9615; TSSOP10
U2: TPS60400DBVR; SOT95P280X145-5N
U3: MS5803-02BA
U4: LTC4317CDHCPBFDFN-16_DHC-M; DFN-16_DHC-M
U5: MCP3425A0T-E/CH; SOT-23-6_MC
U$1: OPENS-LOGO
U$2: DS3502; MSOP10

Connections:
AIN: C10.1, IC2.6 (-IN), JP1.1, U$2.6 (RH), U$2.9 (VBIAS)
AOUT: C6.2, D4.C, D5.A, R11.2, U5.1 (VIN+)
DSCL+: J1.2, J3.2, R13.1, R14.2, U1.7 (DSCL+)
DSCL-: J1.1, J3.1, R14.1, R15.2, U1.6 (DSCL-)
DSDA+: J1.8, J3.8, R16.1, R17.2, U1.8 (DSDA+)
DSDA-: J1.7, J3.7, R17.1, R18.2, U1.9 (DSDA-)
GND: C1.2, C4.1, C5.1, C6.1, C7.2, C8.2, C9.2, C10.2, C11.2, C17.1, C18.1, D4.A, J1.5, J3.5, JP2.1, R1.1, R2.2, R6.1, R7.1, R10.2, R12.1, R15.1, R18.1, R21.1, RHB.2, RLB.2, U1.5 (GND), U2.4 (GND), U3.GND, U4.1 (GND_2), U4.17 (GND), U5.5 (VDD), U5.6 (VIN-), U$2.2 (GND)
unnamed: C1.1, C2.1, IC2.3 (+IN), R1.2
unnamed: C2.2, R4.2
unnamed: C3.2, IC2.1 (OUT), R3.1, R4.1, R5.2
unnamed: D1.A, D2.C, IC2.2 (-IN), R2.1, R3.2
unnamed: IC2.5 (+IN), R5.1, R6.2
unnamed: R12.2, U$2.4 (A1)
unnamed: R21.2, U$2.5 (A0)
unnamed: C3.1, D1.C, D2.A
unnamed: RHB.1, RHT.2, U4.3 (XORH2)
unnamed: C4.2, D3.C, IC2.9 (-IN), R7.2, R8.2
unnamed: D3.A, IC2.8 (OUT)
unnamed: C5.2, IC2.12 (+IN), R8.1
unnamed: IC2.13 (-IN), R9.2, R10.1
unnamed: RLB.1, RLT.2, U4.4 (XORL2)
unnamed: IC2.14 (OUT), R9.1, R11.1
unnamed: C16.2, U2.5 (CFLY+)
unnamed: C16.1, U2.3 (CFLY-)
POT: IC2.7 (OUT), IC2.10 (+IN), U$2.7 (RW)
SCL: R19.1, U3.SCLK, U4.14 (SCLOUT1), U5.3 (SCL), U$2.10 (SCL)
SCL_IN: U1.4 (SCL), U4.15 (SCLIN)
SDA: R20.1, U3.SDI/SDA, U4.13 (SDAOUT1), U5.4 (SDA), U$2.1 (SDA)
SDA_IN: U1.2 (SDA), U4.12 (SDAIN)
VCC: C7.1, C8.1, C9.1, C11.1, C18.2, D5.C, IC2.4 (V+), J1.4, J3.4, R13.2, R16.2, R19.2, R20.2, RHT.1, RLT.1, U1.1 (VDDA), U1.10 (VDDB), U2.2 (IN), U3.PS, U3.VDD, U4.7 (VCC), U$2.3 (VCC)
VNEG: C17.2, IC2.11 (V-), U2.1 (OUT)

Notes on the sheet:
PCA9615 IC
I2C Pullups
RJ-45 Connector Input
Differential I2C Termination Resistors
Switching Regulator
EC Circuit
Compact-Sensor v1.0 2-7-2020 Zack Pelster
I2C Potentiometer
Pressure/Temperature Sensor
16-bit I2C ADC
I2C Address Translator
Check LTC4317 datasheet for setting the resistive divider. (Address shift shown 0110 0010b or 0x62)
RJ-45 Connector
RJ-45 Connector Output
EC Probes

Board: 2 copper layers, 56 parts (28 on the bottom side), 31 nets, no tracks yet.

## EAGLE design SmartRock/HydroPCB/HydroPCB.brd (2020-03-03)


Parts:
A0, A1, A2: PINHD-1X3; 1X03
I2C0, I2C1: PINHD-1X4; 1X04
JUMP: PINHD-1X3; 1X03
M0: BLUEFRUIT_M0; BLUEFRUIT_MO
Q1: FDN337N; SSOT-3
R2: 10k; R1206
REED: PINHD-1X2; 1X02

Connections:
A0: A0.3, M0.A0
A1: A1.3, M0.A1
A2: A2.3, M0.A2
CONTROLGND: A0.2, A1.2, A2.2, I2C0.3, I2C1.3, JUMP.2
EN: M0.10, Q1.1 (G), R2.2
GND: JUMP.1, M0.GND, Q1.2 (S), R2.1, REED.2
unnamed: M0.9, REED.1
NMOS: JUMP.3, Q1.3 (D)
SCL: I2C0.2, I2C1.2, M0.SCL
SDA: I2C0.1, I2C1.1, M0.SDA
VCC: M0.BAT
VIN: A0.1, A1.1, A2.1, I2C0.4, I2C1.4, M0.3V

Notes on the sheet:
3 pin Analog Signals
3 pin Jumper
N-MOS logic gate
I2C connections
Feather M0


Board: 2 copper layers, 79.0 x 33.3 mm, 10 parts (0 on the bottom side), 11 nets.

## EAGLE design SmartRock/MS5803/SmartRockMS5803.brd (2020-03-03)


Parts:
C1: 100nF; C0805
JP1: PINHD-1X4; 1X04
PRESSURE: MS5803-01BA; SMD
R1, R2: 7.7k; R0805

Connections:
GND: C1.1, JP1.3, PRESSURE.CSB, PRESSURE.GND
unnamed: C1.2, JP1.2, PRESSURE.PS, PRESSURE.VDD, R1.2, R2.2
unnamed: JP1.1, PRESSURE.SDI/SDA, R2.1
SCLK: JP1.4, PRESSURE.SCLK, R1.1



Board: 2 copper layers, 16.6 x 11.5 mm, 5 parts (3 on the bottom side), 4 nets.

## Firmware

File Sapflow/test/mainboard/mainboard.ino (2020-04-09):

#include <OPEnS_RTC.h>

const int ALARM_DURATION = 10; 		// Number of seconds before alarm goes off

// Instance of DS3231 RTC
RTC_DS3231 RTC_DS; 


#define ALARM_PIN 12


volatile bool alarmFlag;
void alarmISR() { 
	detachInterrupt(digitalPinToInterrupt(ALARM_PIN)); 
	alarmFlag = true;
	Serial.println("Alarm triggered");
}


void setup() 
{ 
	pinMode(ALARM_PIN, INPUT_PULLUP);  // Pull up resistors required for Active-Low interrupts
	pinMode(LED_BUILTIN, OUTPUT);
  pinMode(5, OUTPUT);
  pinMode(6, OUTPUT);
  pinMode(A3, OUTPUT);
  digitalWrite(A3, LOW);
	digitalWrite(LED_BUILTIN, HIGH);

	RTC_DS.begin();
 #if 1
	DateTime t(__DATE__, __TIME__); 
  t = t + TimeSpan(5);   //account for compilation time
  RTC_DS.adjust(t);
  #endif

	Serial.begin(115200);
	while (!Serial); // Won't start anything until serial is open, comment this line out if powering from battery
	delay(1000);
	Serial.println("Initialized Serial");

	alarmFlag = true;

	Serial.println("\n ** Setup Complete ** ");
}

void loop() 
{
	if (alarmFlag) {
    digitalWrite(6, HIGH);
    delay(1000);
    digitalWrite(5, LOW);
    delay(1000);
    RTC_DS.clearAlarm();
    digitalWrite(A3, HIGH);
    delay(200);
    digitalWrite(A3, LOW);
		
		// Setup interrupt and alarm
		// Mysterious issue: Must call this function twice
		attachInterrupt( digitalPinToInterrupt(ALARM_PIN), alarmISR, LOW );
		attachInterrupt( digitalPinToInterrupt(ALARM_PIN), alarmISR, LOW );

		DateTime alarmTime = RTC_DS.now()+TimeSpan(ALARM_DURATION);
		Serial.print("Alarm set to ");
		Serial.println(alarmTime.text());
		RTC_DS.setAlarm(alarmTime);
    digitalWrite(6, LOW);
    digitalWrite(5, HIGH);
		alarmFlag = false;
	}
}

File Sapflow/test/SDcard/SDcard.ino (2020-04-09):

/*
 * Example use of chdir(), ls(), mkdir(), and  rmdir().
 */
#include <SPI.h>
#include "SdFat.h"
#include "sdios.h"
// SD card chip select pin.
const uint8_t chipSelect = 10;
//------------------------------------------------------------------------------

// File system object.
SdFat sd;

// Directory file.
SdFile root;

// Use for file creation in folders.
SdFile file;

// Create a Serial output stream.
ArduinoOutStream cout(Serial);

// Buffer for Serial input.
char cinBuf[40];

// Create a serial input stream.
ArduinoInStream cin(Serial, cinBuf, sizeof(cinBuf));
//==============================================================================
// Error messages stored in flash.
#define error(msg) sd.errorHalt(F(msg))
//------------------------------------------------------------------------------
void setup() {
  Serial.begin(9600);
  pinMode(5, OUTPUT);

  // Wait for USB Serial
  while (!Serial) {
    SysCall::yield();
  }
  digitalWrite(5, HIGH);
  cout << F("Type any character to start\n");
  // Wait for input line and discard.
  cin.readline();
  cout << endl;
  digitalWrite(5, LOW);
  delay(1000);
  // Initialize at the highest speed supported by the board that is
  // not over 50 MHz. Try a lower speed if SPI errors occur.
  if (!sd.begin(chipSelect, SD_SCK_MHZ(1))) {
    sd.initErrorHalt();
  }
  if (sd.exists("Folder1")
    || sd.exists("Folder1/file1.txt")
    || sd.exists("Folder1/File2.txt")) {
    error("Please remove existing Folder1, file1.txt, and File2.txt");
  }

  int rootFileCount = 0;
  if (!root.open("/")) {
    error("open root failed");
  }
  while (file.openNext(&root, O_RDONLY)) {
    if (!file.isHidden()) {
      rootFileCount++;
    }
    file.close();
    if (rootFileCount > 10) {
      error("Too many files in root. Please use an empty SD.");
    }
  }
  if (rootFileCount) {
    cout << F("\nPlease use an empty SD for best results.\n\n");
    delay(1000);
  }
  // Create a new folder.
  if (!sd.mkdir("Folder1")) {
    error("Create Folder1 failed");
  }
  cout << F("Created Folder1\n");

  // Create a file in Folder1 using a path.
  if (!file.open("Folder1/file1.txt", O_WRONLY | O_CREAT)) {
    error("create Folder1/file1.txt failed");
  }
  file.close();
  cout << F("Created Folder1/file1.txt\n");

  // Change volume working directory to Folder1.
  if (!sd.chdir("Folder1")) {
    error("chdir failed for Folder1.\n");
  }
  cout << F("chdir to Folder1\n");

  // Create File2.txt in current directory.
  if (!file.open("File2.txt", O_WRONLY | O_CREAT)) {
    error("create File2.txt failed");
  }
  file.close();
  cout << F("Created File2.txt in current directory\n");

  cout << F("\nList of files on the SD.\n");
  sd.ls("/", LS_R);

  // Remove files from current directory.
  if (!sd.remove("file1.txt") || !sd.remove("File2.txt")) {
    error("remove failed");
  }
  cout << F("\nfile1.txt and File2.txt removed.\n");

  // Change current directory to root.
  if (!sd.chdir()) {
    error("chdir to root failed.\n");
  }

  cout << F("\nList of files on the SD.\n");
  sd.ls(LS_R);

  // Remove Folder1.
  if (!sd.rmdir("Folder1")) {
    error("rmdir for Folder1 failed\n");
  }

  cout << F("\nFolder1 removed.\n");
  cout << F("\nList of files on the SD.\n");
  sd.ls(LS_R);
  cout << F("Done!\n");
  digitalWrite(5, HIGH);
  pinMode(24, INPUT);
  pinMode(23, INPUT);
  pinMode(10, INPUT);
}
void loop() {
}

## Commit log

2020-02-22 initial commit example :)
    [EvaporometerLite.brd, EvaporometerLite.sch]
2020-02-23 Added new flex probe
    [flex_probe.brd, flex_probe.sch]
2020-02-23 added smart probe files
    [smart_probe.brd, smart_probe.sch]
2020-02-29 Sync with laser cutter computer files
    [Evap-Lite V2.1.brd, Evap-Lite V2.1.sch, Evap-Lite V2.2.brd, Evap-Lite V2.2.sch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]
2020-03-03 updated w/ front page READMe
    [Bill of Materials - Hypnos V3.xlsx, HydroPCB.brd, HydroPCB.sch, Hypnos V3.brd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]
2020-03-03 "restore files"
    [flex_probe.brd, flex_probe.sch, smart_probe.brd, smart_probe.sch]
2020-03-12 Made flex probe thinner
    Also made a panel layout, so we can fit more PCBs into the same area.
    [flex_probe.sch, flex_probe_panel.brd]
2020-03-19 added v2 of smart probe in Sapflow
    [smart_probe.brd, smart_probe.sch]
2020-03-20 added sapflow wing v4
    [sapflow_v4.brd, sapflow_v4.sch]
2020-03-20 Removed duplicate versions
    [smart_probe.brd, smart_probe.csv, smart_probe.sch]
2020-03-20 Removed sapflow board v3
    [flex_probe.brd, flex_probe.sch, flex_probe_panel.brd, sapflow_v3.brd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]
2020-03-20 Created BOM for orders of 12 boards
    Reduced the BOM length by changing some part values on sapflow_v4
    [sapflow_bom.xls, sapflow_v4.brd, sapflow_v4.sch]

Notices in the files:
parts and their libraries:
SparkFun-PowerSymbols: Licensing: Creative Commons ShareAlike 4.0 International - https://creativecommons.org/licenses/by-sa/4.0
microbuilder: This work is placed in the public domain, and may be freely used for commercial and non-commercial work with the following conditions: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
